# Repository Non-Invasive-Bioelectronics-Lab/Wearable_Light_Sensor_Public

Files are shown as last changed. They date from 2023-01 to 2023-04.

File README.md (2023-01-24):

# Wearable Light Sensor Public

This folder contains the version 2 development files of the wearable light monitoring device, including:

• Hardware (FR4): PCB and schematic design of the device, PCB and schematic design of the programming/debugging adaptor

• Firmware: Instructions on how to set up the environment and configure the Arduino IDE to support BL652 Bluetooth module/MCU

• Device enclosure: SolidWorks design files + .stl files for direct 3D printing

• Customised companion android app, Bluefruit LE connect (source code + .apk file)

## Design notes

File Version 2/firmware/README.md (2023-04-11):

# Arduino programming
Code to allow programming of the light monitoring device based on Laird Connectivity BL652 (Nordic semi nRF52832) bluetooth module/MCU using the Arduino IDE.
This makes use of the [Adafruit Feather nRF52 Bluefruit LE - nRF52832](https://www.adafruit.com/product/3406) product and the associated Adafruit libaries.

## Setting up enviroment
Prerequisites:
 - [Arduino IDE 1.8.15](https://www.arduino.cc/en/software) (do NOT install Windows Store version) (tested version: 1.8.15)
 - [Git](https://git-scm.com/downloads)
 - [J-Link software V6.88a and V7.20b](https://www.segger.com/downloads/jlink/#J-LinkSoftwareAndDocumentationPack) (Tested version: V6.88a)
 - [nRF Connect](https://www.nordicsemi.com/Products/Development-tools/nrf-connect-for-desktop/download) (optional)
 - [nrf command line tools](https://www.nordicsemi.com/Products/Development-tools/nRF-Command-Line-Tools/Download?lang=en#infotabs) (Tested version: 10.12.1)
 - nRF52 SDK 17.0.2 (this may not be required)
 - [Adafruit nRF52 by Adafruit Arduino Board Support Package (see below)](https://github.com/adafruit/Adafruit_nRF52_Arduino)

 To install the Adafruit nRF52 library follow the following steps:
 1. Go into Preferences
 2. Add https://adafruit.github.io/arduino-board-index/package_adafruit_index.json as an 'Additional Board Manager URL'
 3. Restart the Arduino IDE
 4. Open the Boards Manager from the Tools -> Board menu and install 'Adafruit nRF52 by Adafruit' and once it is installed, select 'Adafruit Feather nRF52832' from the Tools -> Board menu, which will update your system config to use the right compiler and settings for the nRF52.
 
 5. Delete the core folder `nrf52` installed by Board Manager in Adruino15, depending on your OS. It could be
  * macOS  : `~/Library/Arduino15/packages/adafruit/hardware`
  * Linux  : `~/.arduino15/packages/adafruit/hardware`
  * Windows: `%LOCALAPPDATA%\Arduino15\packages\adafruit\hardware`
 6. `cd <SKETCHBOOK>`, where `<SKETCHBOOK>` is your Arduino Sketch folder:
  * macOS  : `~/Documents/Arduino`
  * Linux  : `~/Arduino`
  * Windows: `~/Documents/Arduino`
 7. Create a folder named `hardware/Adafruit`, if it does not exist, and change directories to it
 8. Clone the repo from Adafruit & its submodules: 
 9. `git clone https://github.com/adafruit/Adafruit_nRF52_Arduino.git`
    
    `cd Adafruit_nRF52_Arduino`
    
    `git submodule update --init`
    
    or
    
    `git clone --recurse-submodules https://github.com/adafruit/Adafruit_nRF52_Arduino.git`

 10. Within the repo you downloaded navigate to \variants\feather_nrf52832
 11. Edit the file variant.h and comment out the line #define USE_LFXO 
 12. Change the pin definitions on line 98 - 100 to:
   ```
   #define PIN_SPI_MISO         (24)
   #define PIN_SPI_MOSI         (23)
   #define PIN_SPI_SCK          (25)
   ```
 13. Change the pin defitions on line 112 - 113 to:
   ```
   #define PIN_WIRE_SDA         (26u)
   #define PIN_WIRE_SCL         (27u)
   ```
 14. Uncomment the line #define USE_LFRC (you may need to add in '#'). This sets up the device to use the internal RC oscillator to control the BLE radio
 15. Navigate to `hardware\Adafruit\Adafruit_nRF52_Arduino` and open `programmers.txt` and change line 6 and 7 to:
 
```
nrfjprog.program.cmd=nrfjprog
nrfjprog.program.cmd.windows=nrfjprog.exe
```
 
Next step is to burn the bootloader onto the board. Plug in the board (or development board), you should be able to programme the board using either the dev kit or the dedicated J-LINK. 
Now open the Arduino IDE, go to Tools > Board > Adafruit nRF52 > Adafruit Feather nRF52832
Go to Tools > Port, and select the COM port where your debugger is connected. Note if using the dedicated J-LINK you may need to enable the COM port (J-Link Configurator, right click on device, configure, enable virtual COM port)
To flash the bootloader go to Tools > Burn Bootloader. If this fails try changing settings in Tools > Programmer and switching between J-Link for Bluefruit nRF52 and Bootloader DFU for Bluefruit nRF52
Once this has succeeded you should then be able to flash Arduino files onto the board.

To test, I recommend flashing the controller example. File > Examples > Adafruit Bluefruit nRF52 Libraries > Peripheral > controller
Hit programme. It may fail as you have to put the board in DFU mode. To do this short P0.20/SIO_20/pin 8 to ground, press and release the reset button and then remove the ground short.
Try programming again, if it fails again try switching Tools > Programmer settings as above and putting in DFU mode.

Once successfully programmed with controller example, open serial terminal and download Bluefruit Connect to your phone. Connect to Bluefruit52 > Controller > Control Pad. Press the buttons and you should see the commands appear on the serial terminal on the PC.

# Configuration 

The light monitoring device is developed based on the Adafruit Feather nRF52 Bluefruit LE [nRF52832]. Therefore, in terms of firmware and hardware configurations, it needed to be modified to meet the application requirements and allow the development of firmware based on the Adafruit nRF52 library using Arduino IDE. For example, by default, only one SPI and I2C are active on the Adafruit nRF52 library, although this project needed 2 SPI and 2 I2C according to the hardware routing.
To make the Adafruit nRF52 library ready for firmware development, follow the following steps:

First, set up the environment, then go to:

~\Documents\Arduino\hardware\adafruit\Adafruit_nRF52_Arduino\variants\feather_nrf52832
Open the variant.h with a text editor software (e.g., notepad++) and change the pin definitions on the lines below. Alternatively, you can download the pre-prepared variant.h in this folder and replace the original variant.h:

Defining pins that are different from the nrf52 feather

```
#define PIN_LED2           (11)
#define PIN_A4             (28)
#define PIN_AREF           PIN_A7
#define PIN_VBAT           PIN_A4
#define CHARG_DETECT       (18)
#define SD_DETECT          (17)
```

Adding a second SPI interface

```
#define SPI_INTERFACES_COUNT 2
#define PIN_SPI_MISO         (15)
#define PIN_SPI_MOSI         (0)
#define PIN_SPI_SCK          (13)
static const uint8_t SS    =  1 ;
static const uint8_t MOSI  = PIN_SPI_MOSI ;
static const uint8_t MISO  = PIN_SPI_MISO ;
static const uint8_t SCK   = PIN_SPI_SCK ;
#define PIN_SPI1_MISO        (23)
#define PIN_SPI1_MOSI        (24)
#define PIN_SPI1_SCK         (25)
static const uint8_t SS1   = 22 ;
static const uint8_t MOSI1 = PIN_SPI1_MOSI ;
static const uint8_t MISO1 = PIN_SPI1_MISO ;
static const uint8_t SCK1  = PIN_SPI1_SCK ;
```
Adding a second wire/I2C interface
```
#define WIRE_INTERFACES_COUNT 2
#define PIN_WIRE_SDA         (2u)
#define PIN_WIRE_SCL         (4u)
#define PIN_WIRE1_SDA        (29u)
#define PIN_WIRE1_SCL        (30u)
```
Navigate to `~\Documents\Arduino\hardware\adafruit\Adafruit_nRF52_Arduino\libraries\SPI` and open `SPI_nrf52832.cpp` with a source code editor and add the line below after `SPIClass SPI(NRF_SPIM2,  PIN_SPI_MISO,  PIN_SPI_SCK,  PIN_SPI_MOSI);` (line 227):

```
SPIClass SPI1(NRF_SPIM2,  PIN_SPI1_MISO,  PIN_SPI1_SCK,  PIN_SPI1_MOSI);
```

Navigate to `~\Documents\Arduino\hardware\adafruit\Adafruit_nRF52_Arduino\libraries\Bluefruit52Lib\src` and open `bluefruit.cpp` with a source code editor and comment line 799 (`_setConnLed(true);`) to turn off the LED during the light measurement.

In terms of hardware configuration, due to space constraints on the board, it is necessary to use a programming adaptor as the programming and UART headers are 1.27mm through hole micro terminal strips. Also, in addition to jtag pins, UART pins need to connect to the j-link for debugging/programming the Bl652 Bluetooth module/MCU.

The main firmware features are including:

•	Automatic gain control (AGC)

•	Date/time stamp

•	Real-time battery state of charge (SoC)

•	MicroSD detection

•	Precision timing

•	Command-based communication with smart devices (e.g., smartphones)

•	Auto-checking peripherals (light sensor, temp sensor, microSD card, accelerometer)

•	Saving data on a comma-separated values (CSV) file

•	Auto set date/time using a companion android app (customised Bluefruit LE Connect)

•	Built-in calibration for ADC raw values

•	Saving measurement files over BLE or USB

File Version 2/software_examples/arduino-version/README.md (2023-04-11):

# Arduino programming
Code to allow programming of the light sensor board/nRF52832 chipset using the Arduino IDE.
This makes use of the [Adafruit Feather nRF52 Bluefruit LE - nRF52832](https://www.adafruit.com/product/3406) product and the associated Adafruit libaries

## Setting up enviroment
Prerequisites:
 - Arduino IDE 1.8.13 (do NOT install Windows Store version)
 - [J-Link software V6.88](https://www.segger.com/downloads/jlink/#J-LinkSoftwareAndDocumentationPack)
 - nRF Connect
 - nRF52 SDK 17.0.2 (this may not be required)
 - [Adafruit nRF52 by Adafruit Arduino Board Support Package (see below)](https://github.com/adafruit/Adafruit_nRF52_Arduino)
 
 To install the Adafruit nRF52 library follow the following steps:
 1. Go into Preferences
 2. Add https://www.adafruit.com/package_adafruit_index.json as an 'Additional Board Manager URL'
 3. Restart the Arduino IDE
 4. Open the Boards Manager from the Tools -> Board menu and install 'Adafruit nRF52 by Adafruit'
 5. Delete the core folder `nrf52` installed by Board Manager in Adruino15, depending on your OS. It could be
  * macOS  : `~/Library/Arduino15/packages/adafruit/hardware`
  * Linux  : `~/.arduino15/packages/adafruit/hardware`
  * Windows: `%LOCALAPPDATA%\Arduino15\packages\adafruit\hardware`
 6. `cd <SKETCHBOOK>`, where `<SKETCHBOOK>` is your Arduino Sketch folder:
  * macOS  : `~/Documents/Arduino`
  * Linux  : `~/Arduino`
  * Windows: `~/Documents/Arduino`
 7. Create a folder named `hardware/Adafruit`, if it does not exist, and change directories to it
 8. Clone the repo from Adafruit & its submodules: `git clone --recurse-submodules https://github.com/adafruit/Adafruit_nRF52_Arduino.git`
 9. Within the repo you downloaded navigate to \variants\feather_nrf52832
 10. Edit the file variant.h and comment out the line #define USE_LFXO 
 11. Change the pin definitions on line 98 - 100 to:
   ```
   #define PIN_SPI_MISO         (24)
   #define PIN_SPI_MOSI         (23)
   #define PIN_SPI_SCK          (25)
   ```
 12. Change the pin defitions on line 112 - 113 to:
   ```
   #define PIN_WIRE_SDA         (26u)
   #define PIN_WIRE_SCL         (27u)
   ```
 14. Uncomment the line #define USE_LFRC (you may need to add in '#'). This sets up the device to use the internal RC oscillator to control the BLE radio
 
Next step is to burn the bootloader onto the board. Plug in the board (or development board), you should be able to programme the board using either the dev kit or the dedicated J-LINK. 
Now open the Arduino IDE, go to Tools > Board > Adafruit nRF52 > Adafruit Feather nRF52832
Go to Tools > Port, and select the COM port where your debugger is connected. Note if using the dedicated J-LINK you may need to enable the COM port (J-Link Configurator, right click on device, configure, enable virtual COM port)
To flash the bootloader go to Tools > Burn Bootloader. If this fails try changing settings in Tools > Programmer and switching between J-Link for Bluefruit nRF52 and Bootloader DFU for Bluefruit nRF52
Once this has succeeded you should then be able to flash Arduino files onto the board.

To test, I recommend flashing the controller example. File > Examples > Adafruit Bluefruit nRF52 Libraries > Peripheral > controller
Hit programme. It may fail as you have to put the board in DFU mode. To do this short P0.20/SIO_20/pin 8 to ground, press and release the reset button and then remove the ground short.
Try programming again, if it fails again try switching Tools > Programmer settings as above and putting in DFU mode.

Once successfully programmed with controller example, open serial terminal and download Bluefruit Connect to your phone. Connect to Bluefruit52 > Controller > Control Pad. Press the buttons and you should see the commands appear on the serial terminal on the PC.

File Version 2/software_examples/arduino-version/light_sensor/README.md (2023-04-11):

# light_sensor
This is the firmware based off Arduino libaries to run on the light sensor prototype (v1) board

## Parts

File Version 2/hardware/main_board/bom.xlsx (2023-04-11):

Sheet: Top Side Components
Components for Light Sensor PCB
Our order number: EEZ2177579 |  |  | PO Date: 11/12/20
Lef Ref MU201202A
Christopher Beach, christopher.beach@manchester.ac.uk, The University of Manchester
Designator | Quantity | Manufacturer 1 | Manufacturer Part Number 1 | Supplier 1 | Supplier Part Number 1 | Link 1 | Comment
Top side components
C1 | 1 | KEMET | C0603C105K3RACTU | Digi-Key | 399-7376-1-ND | https://www.digikey.co.uk/product-detail/en/kemet/C0603C105K3RACTU/399-7376-1-ND/3317410 | 0603 1 uF capacitor
C2, C8, C9 | 3 | KEMET | C0603C104K3RACTU | Digi-Key | 399-1281-1-ND | https://www.digikey.co.uk/product-detail/en/kemet/C0603C104K3RACTU/399-1281-1-ND/416057 | 0603 0.1 uF cap
C7 | 1 | AVX Corporation | TCJP105M025R0500E | Digi-Key | 478-13321-1-ND | https://www.digikey.co.uk/product-detail/en/avx-corporation/TCJP105M025R0500E/478-13321-1-ND/10062990 | 0805 1 uF tant cap
D1 | 1 | Dialight | 598-8E40-107F | Farnell | 3514756 | https://uk.farnell.com/dialight/598-8e40-107f/led-yellow-590mcd-590nm-0603/dp/3514756 | 0603 Yellow LED
J1 | 1 | JAE Electronics | DX07S016JA1R1500 | Digi-Key | 670-DX07S016JA1R1500CT-ND | https://www.digikey.co.uk/product-detail/en/jae-electronics/DX07S016JA1R1500/670-DX07S016JA1R1500CT-ND/11586676 | USB C connector
U1 | 1 | AMS | AS7341-DLGM | Digi-Key | AS7341-DLGMCT-ND | https://www.digikey.co.uk/product-detail/en/ams/AS7341-DLGM/AS7341-DLGMCT-ND/9996232 | AS7341 Light sensor
U2 | 1 | Laird Connectivity | BL652-SA-01-T/R | Digi-Key | BL652-SA-01-CT-ND | https://www.digikey.co.uk/product-detail/en/laird-connectivity-inc/BL652-SA-01-T-R/BL652-SA-01-CT-ND/6181738 | BL652 BLE Module
U3 | 1 | Analog Devices | ADXL346ACCZ-RL7 | Digi-Key | ADXL346ACCZ-RL7CT-ND | https://www.digikey.co.uk/product-detail/en/analog-devices-inc/ADXL346ACCZ-RL7/ADXL346ACCZ-RL7CT-ND/2334216 | ADXL346 Accelerometer
R1 | 1 | Panasonic Electronic Components | ERJ-3GEYJ200V | Digi-Key | P20GCT-ND | https://www.digikey.co.uk/product-detail/en/panasonic-electronic-components/ERJ-3GEYJ200V/P20GCT-ND/134656 | 0603 20 ohm resistor
R2, R3, R4 | 3 | Panasonic Electronic Components | ERJ-PA3J103V | Digi-Key | P10KBZCT-ND | https://www.digikey.co.uk/product-detail/en/panasonic-electronic-components/ERJ-PA3J103V/P10KBZCT-ND/5036237 | 0603 10k resistor
R6, R7 | 2 | Panasonic Electronic Components | ERJ-3GEYJ512V | Digi-Key | P5.1KGCT-ND | https://www.digikey.co.uk/product-detail/en/panasonic-electronic-components/ERJ-3GEYJ512V/P5-1KGCT-ND/135226 | 0603 5k1 resistor
R9 | 1 | Panasonic Electronic Components | ERJ-3GEYJ625V | Digi-Key | P6.2MGCT-ND | https://www.digikey.co.uk/product-detail/en/panasonic-electronic-components/ERJ-3GEYJ625V/P6-2MGCT-ND/282440 | 0603 6M2 resistor
R10 | 1 | Panasonic Electronic Components | ERJ-3GEYJ395V | Digi-Key | P3.9MGCT-ND | https://www.digikey.co.uk/product-detail/en/panasonic-electronic-components/ERJ-3GEYJ395V/P3-9MGCT-ND/282435 | 0603 3M9 resistor
R11 | 1 | Panasonic Electronic Components | ERJ-3GEYJ683V | Digi-Key | P68KGCT-ND | https://www.digikey.co.uk/product-detail/en/panasonic-electronic-components/ERJ-3GEYJ683V/P68KGCT-ND/134829 | 0603 68k resistor
R12 | 1 | Panasonic Electronic Components | ERJ-PA3J333V | Digi-Key | P33KBZCT-ND | https://www.digikey.co.uk/product-detail/en/panasonic-electronic-components/ERJ-PA3J333V/P33KBZCT-ND/5036309 | 0603 33k resistor
R5 | 1 | DNP
TP1, TP2, TP3, TP4, TP5, TP6 | 6 | DNP
P1, P2 | 2 | DNP |  |  |  | https://uk.farnell.com/multicomp/mc-svt1-s06-g/connector-rcpt-6pos-1row-1-27mm/dp/2852606 | 6 pin receptacle (DNP)

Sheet: Bottom Side Components
Designator | Quantity | Manufacturer 1 | Manufacturer Part Number 1 | Supplier 1 | Supplier Part Number 1 | Link 1 | Comment
Bottom side components
C3, C4, C5 | 3 | KEMET | C0603C105K3RACTU | Digi-Key | 399-7376-1-ND | https://www.digikey.co.uk/product-detail/en/kemet/C0603C105K3RACTU/399-7376-1-ND/3317410 | 0603 1 uF capacitor
C6 | 1 | KEMET | C0603C475K9PACTU | Digi-Key | 399-3482-1-ND | https://www.digikey.co.uk/product-detail/en/kemet/C0603C475K9PACTU/399-3482-1-ND/754775 | 0603 4.7 uF capacitor
U4 | 1 | Microchip Technology | MCP73812T-420I/OT | Digi-Key | MCP73812T-420I/OTCT-ND | https://www.digikey.co.uk/product-detail/en/microchip-technology/MCP73812T-420I-OT/MCP73812T-420I-OTCT-ND/1979800 | MCP73812 charge controller
U5 | 1 | Texas Instruments | TPS76318DBVT | Farnell | 3007904 | https://uk.farnell.com/texas-instruments/tps76318dbvt/v-reg-ldo-0-15a-1-8v-smd-76318/dp/3007904 | 1V8 regulator
R8 | 1 | Panasonic Electronic Components | ERJ-PB3D2002V | Digi-Key | P20429CT-ND | https://www.digikey.co.uk/product-detail/en/panasonic-electronic-components/ERJ-PB3D2002V/P20429CT-ND/6214684 | 0603 20k resistor
B1 | 1 | Multicomp | BC-2404 | Farnell | 2064669 | https://uk.farnell.com/multicomp/bc-2404/retainer-clip-24mm-smt/dp/2064669 | 2450 Cell holder
SW1 | 1 | Nidec Copal Electronics | CHS-01TB | Farnell | 2854726 | https://uk.farnell.com/nidec-copal-electronics/chs-01tb/dip-switch-1pos-spst-slide-smd/dp/2854726?ost=2854726 | Slide Switch

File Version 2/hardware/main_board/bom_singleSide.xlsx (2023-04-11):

Components for Light Sensor PCB
Our order number: EEZ2177579 |  |  | PO Date: 11/12/20
Lef Ref MU201202A
Christopher Beach, christopher.beach@manchester.ac.uk, The University of Manchester
Designator | Quantity | Manufacturer 1 | Manufacturer Part Number 1 | Supplier 1 | Supplier Part Number 1 | Link 1 | Comment
Top side components
C1 | 1 | KEMET | C0603C105K3RACTU | Digi-Key | 399-7376-1-ND | https://www.digikey.co.uk/product-detail/en/kemet/C0603C105K3RACTU/399-7376-1-ND/3317410 | 0603 1 uF capacitor
C3, C4, C5, C11 | 5 | KEMET | C0402C105K4PACTU | Onecall | 2494500 | https://onecall.farnell.com/kemet/c0402c105k4pactu/cap-1-f-16v-10-x5r-0402/dp/2494500 | 0402 1 uF capacitor
C2, C8, C9, C10, C14, C15 | 6 | TDK | CGA2B3X7R1E104K050BB | Onecall | 2210820 | https://onecall.farnell.com/tdk/cga2b3x7r1e104k050bb/cap-0-1-f-25v-10-x7r-0402/dp/2210820 | 0402 0.1 uF cap
C6, C12 | 2 | Murata | ZRB15XR61A475ME01D | Onecall | 2469394 | https://onecall.farnell.com/murata/zrb15xr61a475me01d/cap-4-7-f-10v-20-x5r-0402/dp/2469394 | 0603 4.7 uF capacitor
C7 | 1 | AVX Corporation | TCJP105M025R0500E | Digi-Key | 478-13321-1-ND | https://www.digikey.co.uk/product-detail/en/avx-corporation/TCJP105M025R0500E/478-13321-1-ND/10062990 | 0805 1 uF tant cap
C13 | 1 | Vishay | TMCP1A106KTRF | Onecall | 2491435 | https://onecall.farnell.com/vishay/tmcp1a106ktrf/cap-10-f-10v-10/dp/2491435 | 0805 10uF tant cap
D1 | 1 | Dialight | 598-8E40-107F | Farnell | 3514756 | https://uk.farnell.com/dialight/598-8e40-107f/led-yellow-590mcd-590nm-0603/dp/3514756 | 0603 Yellow LED
J1 | 1 | JAE Electronics | DX07S016JA1R1500 | Digi-Key | 670-DX07S016JA1R1500CT-ND | https://www.digikey.co.uk/product-detail/en/jae-electronics/DX07S016JA1R1500/670-DX07S016JA1R1500CT-ND/11586676 | USB C connector | Use Mouser
U1 | 1 | AMS | AS7341-DLGM | Digi-Key | AS7341-DLGMCT-ND | https://www.digikey.co.uk/product-detail/en/ams/AS7341-DLGM/AS7341-DLGMCT-ND/9996232 | AS7341 Light sensor | Use RS (18th Aug)
U2 | 1 | Laird Connectivity | BL652-SA-01-T/R | Digi-Key | BL652-SA-01-CT-ND | https://www.digikey.co.uk/product-detail/en/laird-connectivity-inc/BL652-SA-01-T-R/BL652-SA-01-CT-ND/6181738 | BL652 BLE Module | In stock
U3 | 1 | Analog Devices | ADXL362BCCZ-R2 | Digi-Key | ADXL362BCCZ-R2CT-ND | https://www.digikey.co.uk/product-detail/en/analog-devices-inc/ADXL362BCCZ-R2/ADXL362BCCZ-R2CT-ND/3828936 | ADXL346 Accelerometer
U5 | 1 | Microchip Technology | MCP73812T-420I/OT | Digi-Key | MCP73812T-420I/OTCT-ND | https://www.digikey.co.uk/product-detail/en/microchip-technology/MCP73812T-420I-OT/MCP73812T-420I-OTCT-ND/1979800 | MCP73812 charge controller | Use CPC (PO)
U4 | 1 | Texas Instruments | TPS76318DBVT | Farnell | 3007904 | https://uk.farnell.com/texas-instruments/tps76318dbvt/v-reg-ldo-0-15a-1-8v-smd-76318/dp/3007904 | 1V8 regulator
U6 | 1 | Maxim | MAX31889ALT+ | RS | 204-2520 | https://uk.rs-online.com/web/p/temperature-humidity-sensor-ics/2042520
U7 | 1 | Texas Instruments | TPS76333DBVT | Onecall | SC16625 | https://onecall.farnell.com/texas-instruments/tps76333dbvt/v-reg-ldo-0-15a-3-3v-smd-76333/dp/SC16625?ost=sc16625 | 3V3 regulator
R1 | 1 | Multicomp Pro | MCWR04X20R0FTL | Onecall | 2447134 | https://onecall.farnell.com/multicomp/mcwr04x20r0ftl/res-20r-1-0-0625w-thick-film/dp/2447134 | 0402 20 ohm resistor
R3, R4, R5 | 3 | Multicomp Pro | MCMR04X103 JTL | Onecall | 2072528 | https://onecall.farnell.com/multicomp/mcmr04x103-jtl/res-10k-5-0-0625w-0402-ceramic/dp/2072528 | 0402 10k resistor
R6, R7 | 2 | Multicomp Pro | MP000528 | Onecall | 3213460 | https://onecall.farnell.com/multicomp-pro/mp000528/res-5k1-1-0-1w-0402-thick-film/dp/3213460 | 0402 5k1 resistor
R8 | 1 | Multicomp Pro | MCWR04X2002FTL | Onecall | 2447133 | https://onecall.farnell.com/multicomp/mcwr04x2002ftl/res-20k-1-0-0625w-thick-film/dp/2447133 | 0402 20k resistor
R9 | 1 | Multicomp Pro | MCHVR02FTFY6204 | Onecall | 2825359 | https://onecall.farnell.com/multicomp/mchvr02ftfy6204/res-6m2-1-0-063w-0402-thick-film/dp/2825359 | 0402 6M2 resistor
R10 | 1 | Multicomp Pro | MCHVR02JTFY3904 | Onecall | 2825495 | https://onecall.farnell.com/multicomp/mchvr02jtfy3904/res-3m9-5-0-063w-0402-thick-film/dp/2825495 | 0402 3M9 resistor
R11 | 1 | Panasonic Electronic Components | ERJ-3GEYJ683V | Digi-Key | P68KGCT-ND | https://www.digikey.co.uk/product-detail/en/panasonic-electronic-components/ERJ-3GEYJ683V/P68KGCT-ND/134829 | 0603 68k resistor
R12 | 1 | Panasonic Electronic Components | ERJ-PA3J333V | Digi-Key | P33KBZCT-ND | https://www.digikey.co.uk/product-detail/en/panasonic-electronic-components/ERJ-PA3J333V/P33KBZCT-ND/5036309 | 0603 33k resistor
R2 | 1 | DNP
B1 | 1 | Multicomp | BC-2404 | Farnell | 2064669 | https://uk.farnell.com/multicomp/bc-2404/retainer-clip-24mm-smt/dp/2064669 | 2450 Cell holder
SW1 | 1 | Nidec Copal Electronics | CHS-01TB | Farnell | 2854726 | https://uk.farnell.com/nidec-copal-electronics/chs-01tb/dip-switch-1pos-spst-slide-smd/dp/2854726?ost=2854726 | Slide Switch
P1, P2 | 2 | DNP |  |  |  | https://uk.farnell.com/multicomp/mc-svt1-s06-g/connector-rcpt-6pos-1row-1-27mm/dp/2852606 | 6 pin receptacle (DNP)

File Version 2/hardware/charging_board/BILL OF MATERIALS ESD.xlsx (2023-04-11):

Site | Designator | Comment | Footprint | Quantity | LCSC Part No. | Man. Part no. | Link
JLCPCB | USB_FEM_1 | U262-241N-4BV64 | usbc_female | 1 | C388660 | U262-241N-4BV64 | https://jlcpcb.com/partdetail/XkbConnectivity-U262_241N4BV64/C388660
JLCPCB | USB_MALE_1 | GT-USB-8012A | PCBComponents_1 | 1 | C2982483 | GT-USB-8012A | https://jlcpcb.com/partdetail/gswitch-GT_USB8012A/C2982483
JLCPCB | D1 | SMAJ5.0A | SMA(DO-214AC) | 1 | C78401 | SMAJ5.0A/TR13 | https://jlcpcb.com/partdetail/Brightking-SMAJ5_0ATR13/C78401
JLCPCB | U1 | TPD1S414YZR | DSBGA-12 | 1 | C411873 | TPD1S414YZR | https://jlcpcb.com/partdetail/TexasInstruments-TPD1S414YZR/C411873
JLCPCB | C1 | 1 uF | "0805" | 1 | C215803 | 0805B105K500NT | https://jlcpcb.com/partdetail/216551-0805B105K500NT/C215803
JLCPCB | C2 | 2.2 uF | "0805" | 1 | C49217 | 0805F225M500NT | https://jlcpcb.com/partdetail/50225-0805F225M500NT/C49217
JLCPCB | F1 | 0466.200NRHF | FP-0466-MFG | 1 | C206985 | 0466.200NRHF | https://jlcpcb.com/partdetail/Littelfuse-0466200NRHF/C206985

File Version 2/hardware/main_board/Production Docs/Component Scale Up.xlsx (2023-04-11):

Designator | Quantity | Comment | Supplier | Part No. | 1 | 2 | 5 | 10 | 20
C1, C3, C4, C5 | 4 | 0603 1uF | Digi-Key | 399-7376-1-ND | £0.8000 | £1.6000 | £1.6440 | £5.4800 | £7.2800
C2, C8, C9, C10, C11 | 5 | 0603 0.1uF | Digi-Key | 399-1281-1-ND | £0.4000 | £0.5900 | £1.4750 | £1.6100 | £2.6300
C6 | 1 | 0603 4.7uF | Digi-Key | 399-3482-1-ND | £0.1200 | £0.2400 | £0.6000 | £0.8600 | £1.7200
C7 | 1 | 0805 1uF tant | Digi-Key | 478-13321-1-ND | £0.7800 | £1.5600 | £3.9000 | £6.1300 | £6.1300
D1 | 1 | 0603 LED | Farnell | 3514756 | £0.2784 | £0.2784 | £0.2784 | £0.5568 | £5.5680
J1 | 1 | USB C | RS | 201-7049 | £5.5700 | £5.5700 | £5.5700 | £11.1400 | £21.2400
U1 | 1 | Light Sensor | Mouser | 985-AS7341-DLGM | £6.9800 | £13.9600 | £34.9000 | £62.8000 | £125.6000
U2 | 1 | BLE Radio | Digi-Key | BL652-SA-01-CT-ND | £5.3600 | £10.7200 | £26.8000 | £53.6000 | £107.2000 | Cheap from Digikey, stock expected 26th May
U3 | 1 | Accelerometer | Digi-Key | ADXL346ACCZ-RL7CT-ND | £4.6500 | £9.3000 | £23.2500 | £41.7600 | £83.5200
U4 | 1 | Charge Controller | Mouser | 579-MCP73812T-420IOT | £0.4350 | £0.8700 | £2.1750 | £4.3500 | £8.7000
U5 | 1 | 1V8 regulator | Digi-Key | 296-2700-1-ND | £0.7100 | £1.4200 | £3.5500 | £6.3400 | £12.6800
U6 | 1 | Temperature sensor | Digi-Key | 175-MAX31889ALT+-ND | £2.4900 | £4.9800 | £12.4500 | £22.3400 | £44.6800
U7 | 1 | Flash Memory | Digi-Key | 1265-1280-1-ND | £1.0700 | £2.1400 | £5.3500 | £9.7600 | £19.5200
R1 | 1 | 0603 20R | Digi-Key | P20GCT-ND | £0.0700 | £0.1400 | £0.2400 | £0.2400 | £0.4800
R2, R3, R4 | 3 | 0603 10k | Digi-Key | P10KGCT-ND | £0.2100 | £0.4200 | £0.9750 | £1.9500 | £2.4800
R6, R7 | 2 | 0603 5k1 | Digi-Key | P5.1KGCT-ND | £0.2800 | £0.2900 | £0.2900 | £0.5800 | £1.1600
R8 | 1 | 0603 20k | Digi-Key | P20KGCT-ND | £0.0700 | £0.1400 | £0.2600 | £0.2600 | £0.5200
R9 | 1 | 0603 6M2 | Digi-Key | P6.2MGCT-ND | £0.0700 | £0.1400 | £0.1700 | £0.1700 | £0.3400
R10 | 1 | 0603 3M9 | Digi-Key | P3.9MGCT-ND | £0.0700 | £0.1400 | £0.2400 | £0.2400 | £0.4800
R11 | 1 | 0603 68k | Digi-Key | P68KGCT-ND | £0.0700 | £0.1400 | £0.2400 | £0.2400 | £0.4800
R12 | 1 | 0603 33k | Digi-Key | P33KGCT-ND | £0.0700 | £0.1400 | £0.2400 | £0.2400 | £0.4800
SW1 | 1 | Slide Switch | Digi-Key | 563-1004-1-ND | £0.6500 | £1.3000 | £3.2500 | £6.2400 | £12.4800
B1 | 1 | Battery Holder | Farnell | 2064669 | £0.6480 | £1.2960 | £3.2400 | £6.4800 | £12.9600
P1, P2 | 2 | Programming Header | Farnell | 2852606 | £2.0520 | £2.0520 | £2.0520 | £4.1040 | £8.2080
NO REF | 1 | LiIon Coin Cell | Farnell | 2009025 | £3.1200 | £6.2400 | £15.6000 | £28.6800 | £57.3600
Total cost |  |  |  |  | £37.0234 | £65.6664 | £148.7394 | £276.1508 | £543.8960
Price per Unit |  |  |  |  | £37.0234 | £32.8332 | £29.7479 | £27.6151 | £27.1948

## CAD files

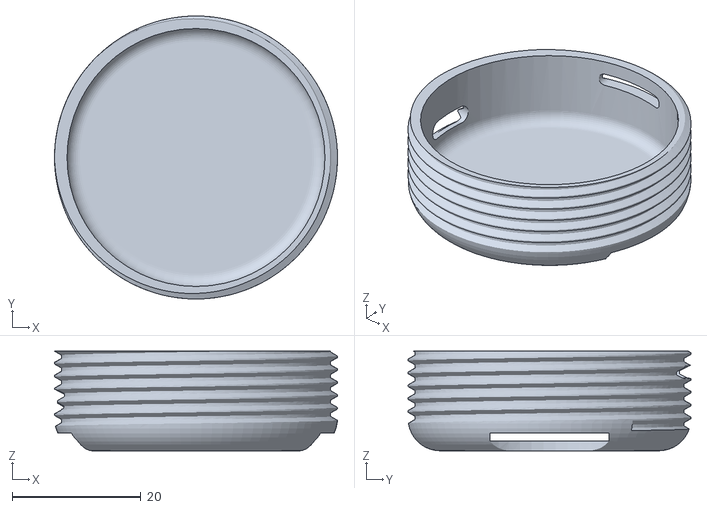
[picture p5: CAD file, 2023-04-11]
Version 2/case/1-20-F.STL
44.0 x 44.0 x 15.5

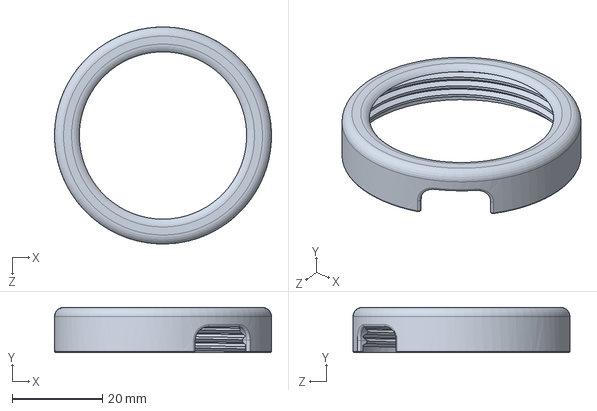
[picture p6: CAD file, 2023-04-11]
Version 2/case/SolidWork files/3 - 27-06-2022_low profile.SLDPRT
48.0 x 10.0 x 48.0 mm

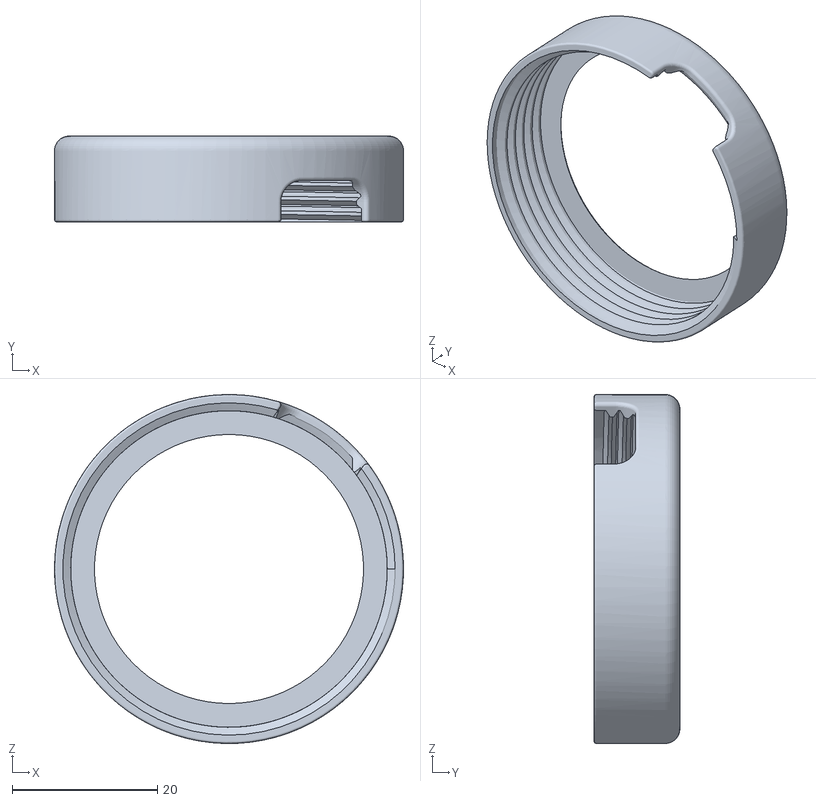
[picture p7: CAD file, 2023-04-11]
Version 2/case/3.STL
48.0 x 11.8 x 48.0

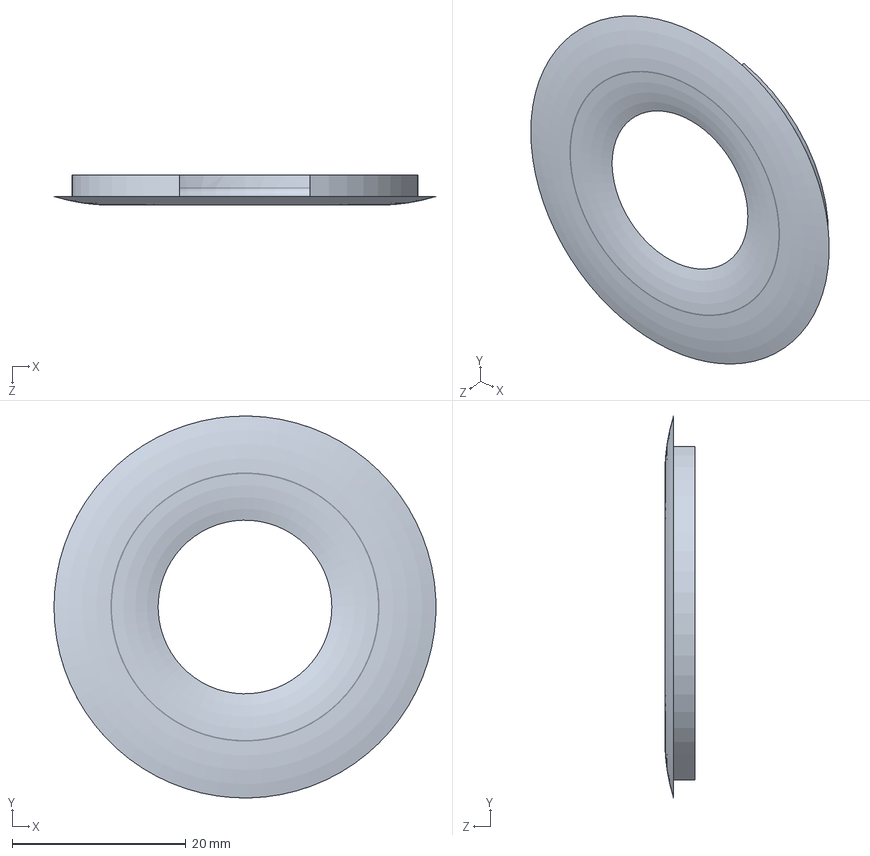
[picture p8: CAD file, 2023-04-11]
Version 2/case/SolidWork files/2 - 11-05-2022.SLDPRT
44.0 x 44.0 x 3.50 mm

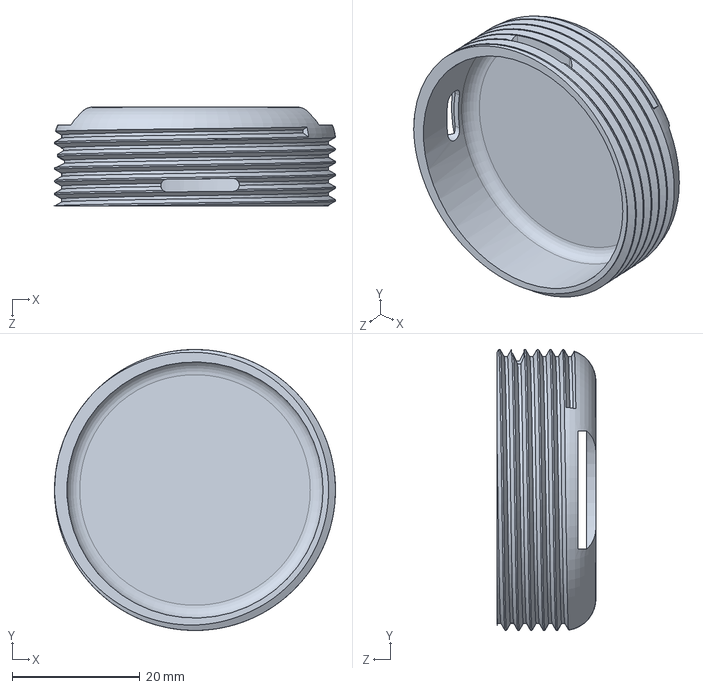
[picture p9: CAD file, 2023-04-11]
Version 2/case/SolidWork files/1 - 11-05-2022.SLDPRT
44.0 x 44.0 x 15.5 mm

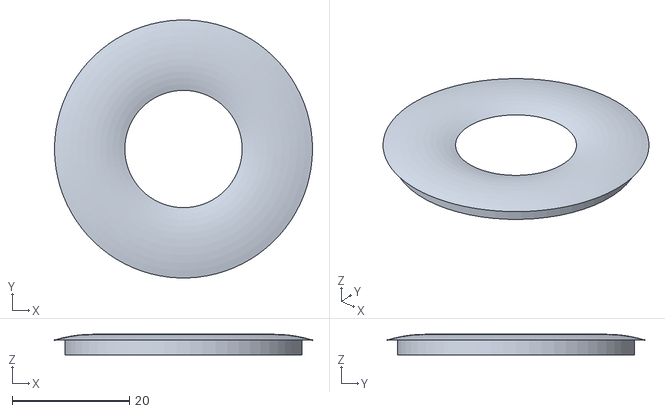
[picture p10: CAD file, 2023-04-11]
Version 2/case/2.STL
44.0 x 44.0 x 3.50

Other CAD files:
Version 2/case/1-3-F.STL
Version 2/case/SolidWork files/3 - 11-05-2022.SLDPRT
Version 2/case/1-8-F.STL
Version 2/case/3 - low profile.STL
Version 2/case/1-2-F.STL
Version 2/case/1-6-F.STL
Version 2/case/1-18-F.STL
Version 2/case/1-4-F.STL
Version 2/case/1-13-F.STL
Version 2/case/1-16-F.STL
Version 2/case/1-15-F.STL
Version 2/case/1-12-F.STL
Version 2/case/1-1-F.STL
Version 2/case/1-10-F.STL
Version 2/case/1-11-F.STL
Version 2/case/1-14-F.STL
Version 2/case/1-17-F.STL
Version 2/case/1-19-F.STL
Version 2/case/1-5-F.STL
Version 2/case/1-7-F.STL
Version 2/case/1-9-F.STL
Version 2/case/2 - updated (with cut off) 11-05-2022.STL
Version 2/case/3 - updated - 11-05-2022.STL
Version 2/case/SolidWork files/2 - 11-05-2022.STL
Version 2/case/SolidWork files/3 - 11-05-2022.STL
Version 2/case/SolidWork files/3 - 27-06-2022_low profile.STL

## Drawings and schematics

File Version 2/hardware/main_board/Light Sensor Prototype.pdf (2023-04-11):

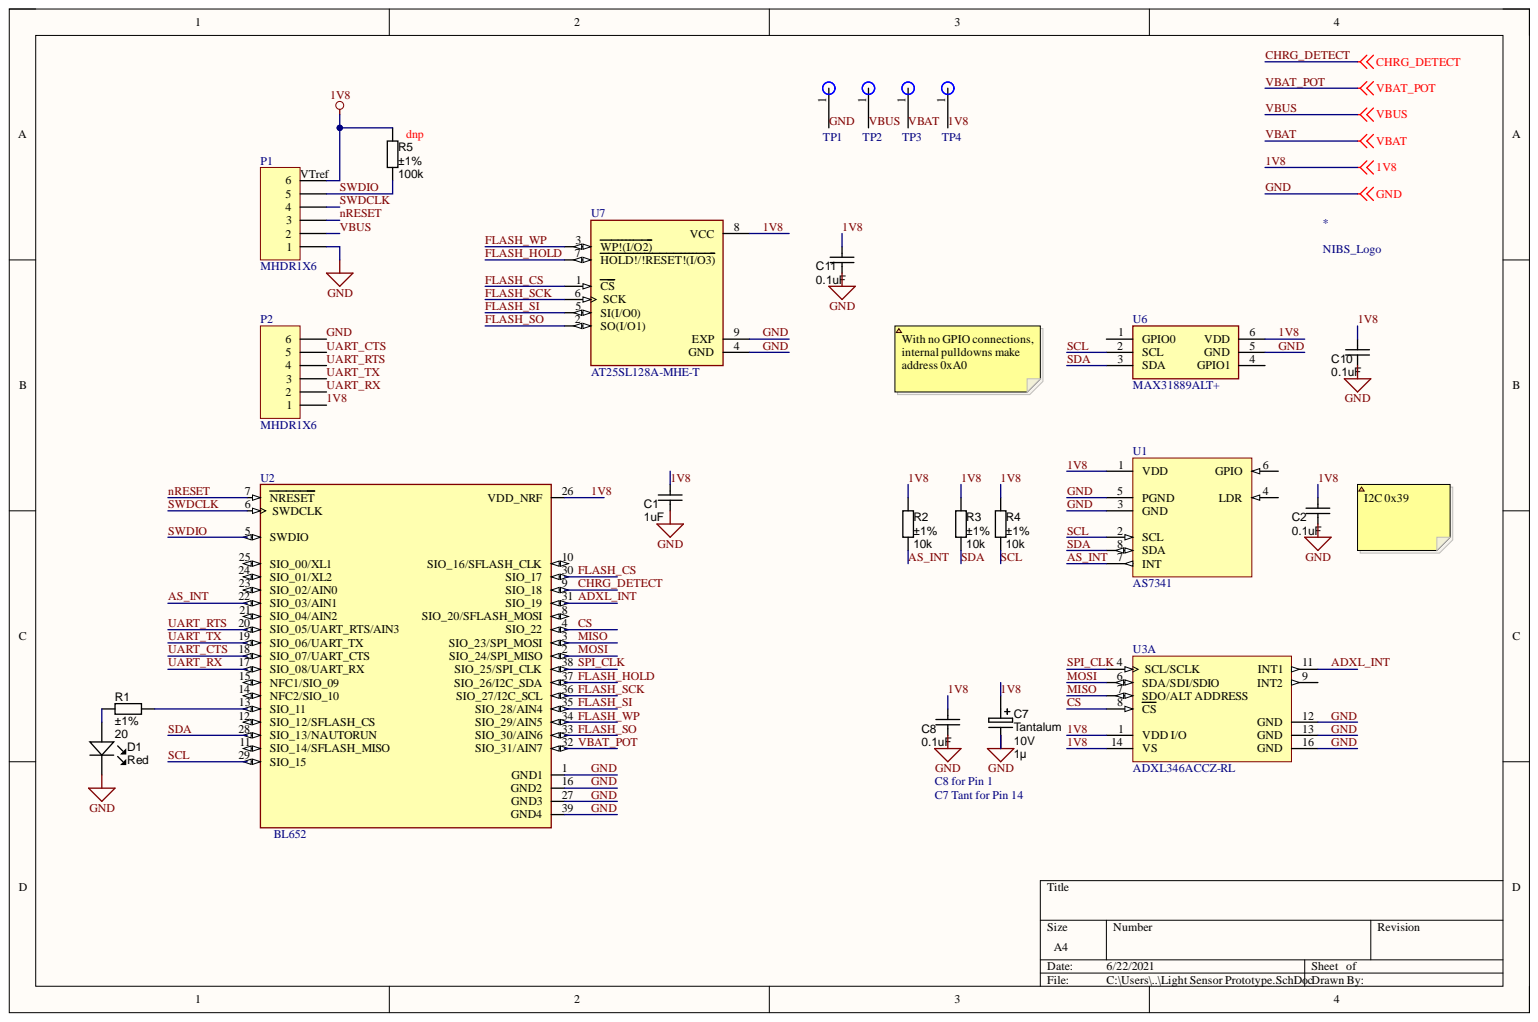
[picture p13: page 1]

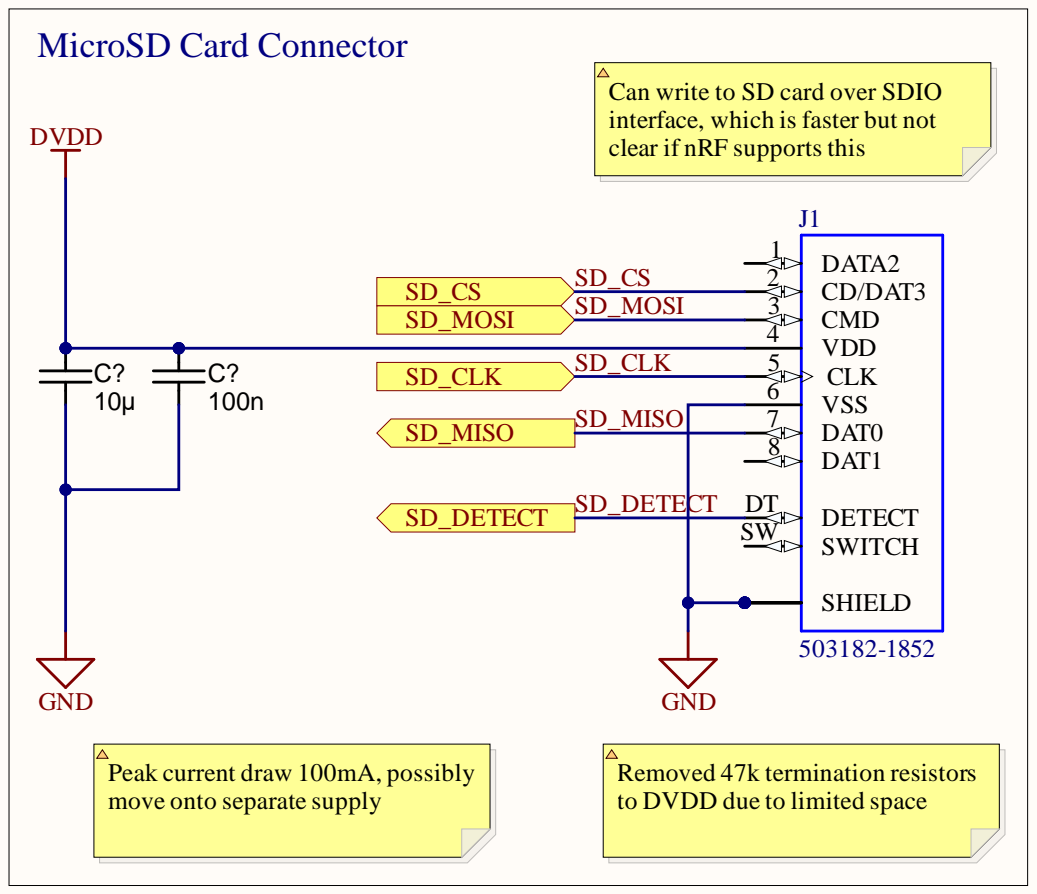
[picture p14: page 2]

Can write to SD card over SDIO
interface, which is faster but not
clear if nRF supports this

Peak current draw 100mA, possibly
move onto separate supply

Removed 47k termination resistors
to DVDD due to limited space

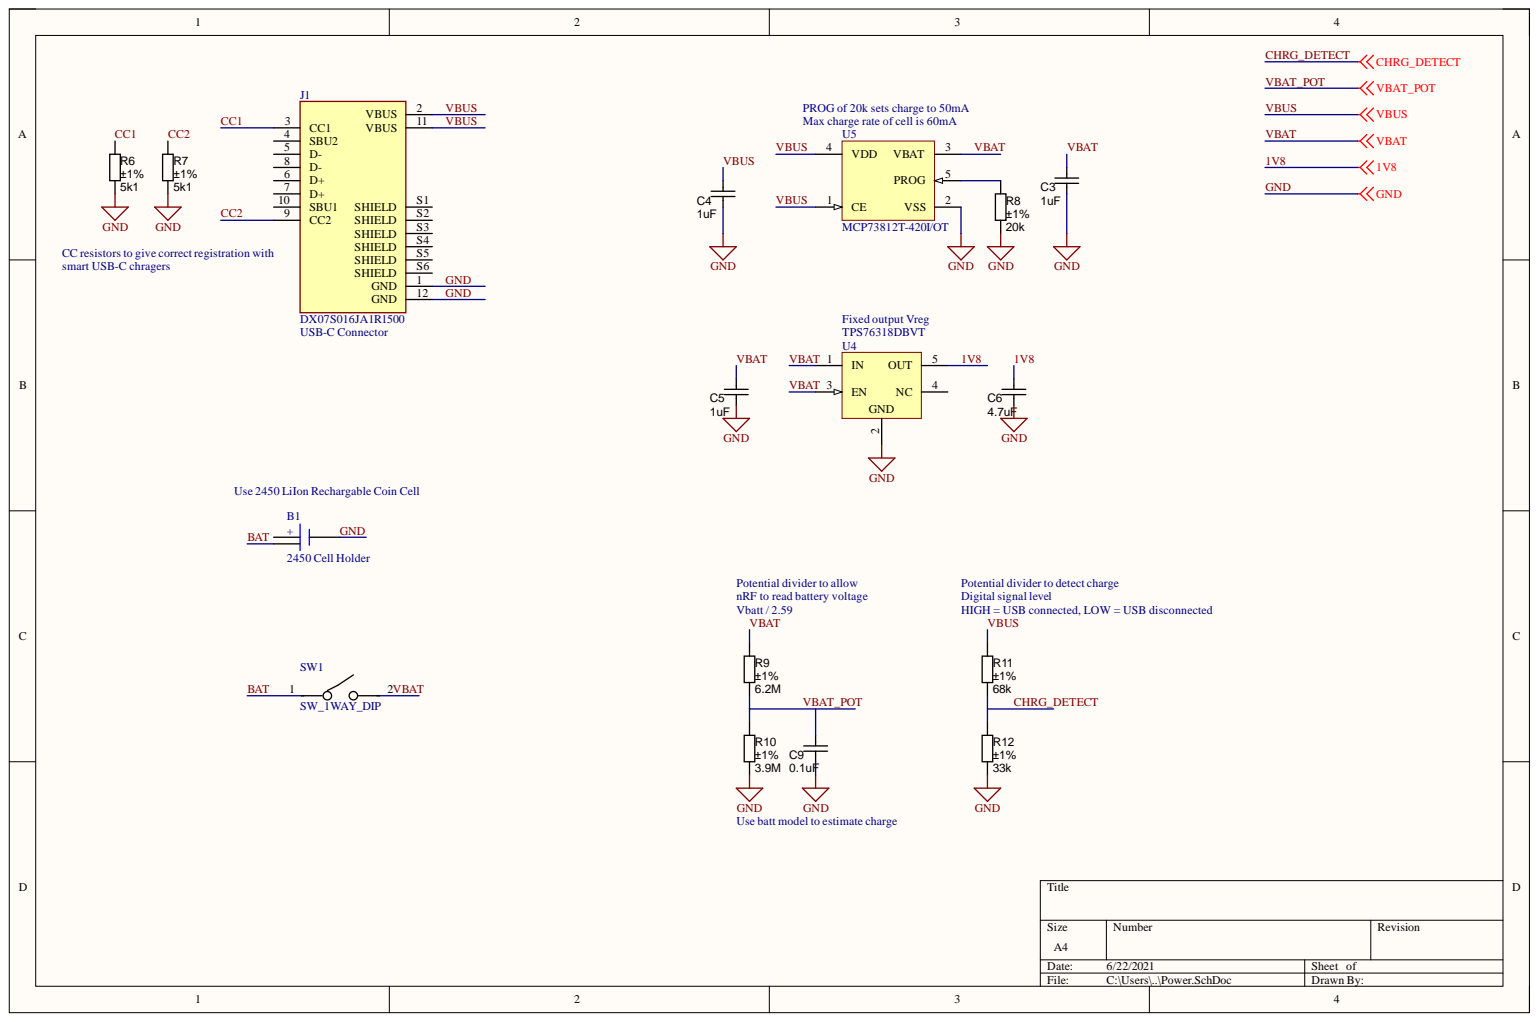
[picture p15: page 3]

PROG of 20k sets charge to 50mA
Max charge rate of cell is 60mA

CC resistors to give correct registration with
smart USB-C chragers

Use 2450 LiIon Rechargable Coin Cell

Potential divider to allow
nRF to read battery voltage
Vbatt / 2.59
VBAT

Potential divider to detect charge
Digital signal level
HIGH = USB connected, LOW = USB disconnected
VBUS

GND
Use batt model to estimate charge

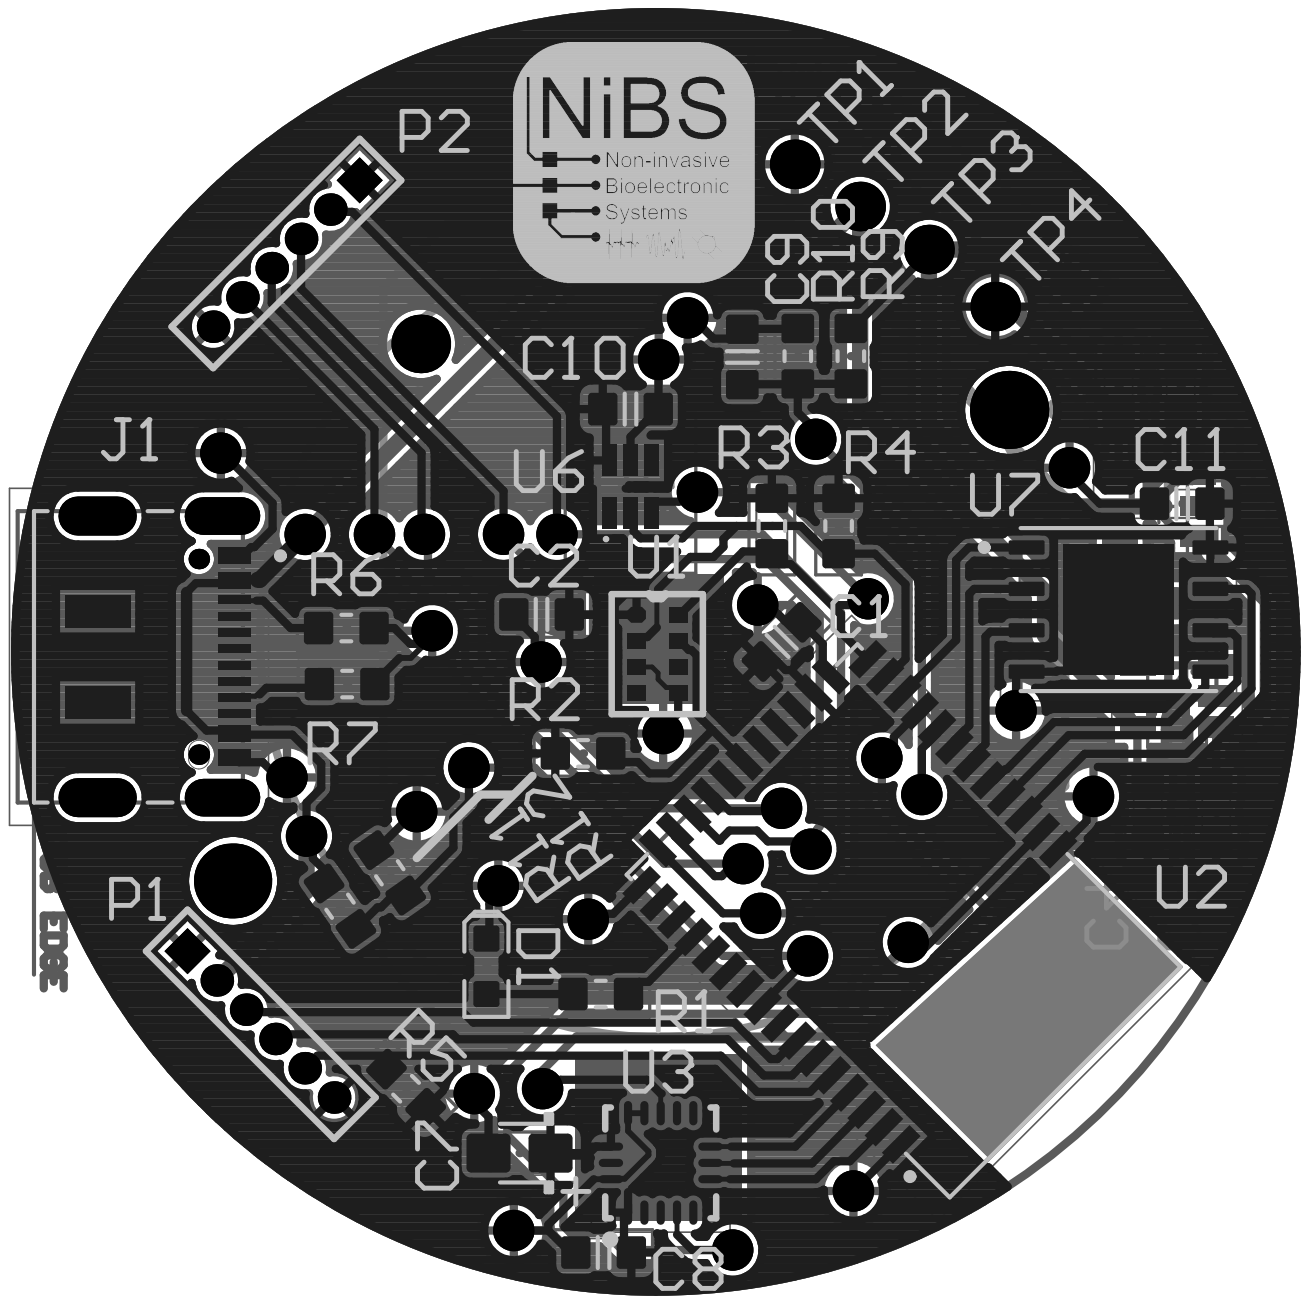
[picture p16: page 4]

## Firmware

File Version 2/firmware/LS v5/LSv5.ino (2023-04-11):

#include <bluefruit.h>
#include <Adafruit_AS7341.h>
#include <LibPrintf.h>
#include <SPI.h>
#include <SD.h>
#include "Time.h"
#include "TimeLib.h"
#include <Wire.h>
#include <ADXL362.h>


// BLE Service
//BLEDfu  bledfu;  // OTA DFU service
BLEDis  bledis;  // device information
BLEUart bleuart; // uart over ble

TwoWire *wi = &Wire1;
ADXL362 ACC; 
Adafruit_AS7341 as7341;
uint8_t light_status;
uint8_t temp_status;
bool Connected = false;
bool sendData = false;
bool state = false;
bool ACC_failed = false;
float correctionGain [12] = {1.06, 1.05, 1.05, 1.05, 1.02, 1.02, 1.01, 1.00, 1.00, 0.99, 0.96};
float correctionFactor [12] = {1,1,1,1,1,1,1,1,1,1,1};
float offsetValues [12] = {0,0,0,0,0,0,0,0,0,0,0};
uint16_t readings[12];
bool timer_start = false;
uint8_t sd_first;
unsigned int A_gain;
uint8_t currentGain = 5;
uint8_t maxGain = 10;
bool RawValueSaturated = false;
bool RawValueNoise = false;
bool iPhone_device = false;
uint8_t newGain = 0;
char central_name[32] = { 0 };
unsigned int A_int;
uint16_t ch[12];
const int chipSelect = 1;
char dataStr[220];
char dataStr1[170];
char num_sam[11];
char filename[13] = "LS14_1.csv";
char num[5];
char timeStr[19] = "";
int acc_status = 0;
char SoC_buf[25];
char time_cent[22];
char setting[35];
volatile bool event = false; 
bool st_check = false;
bool dis_check = true;
bool TS_Failed = false;
char *col_names[] = {"Date", "Time","SoC","Temp", "Gain", "F1", "F2", "F3",
                         "F4", "F5", "F6", "F7" , "F8" , "Clear", "NIR", "accX" , "accY", "accZ",
                        };
char *channel_names[13] = {"F1", "F2", "F3",
                         "F4"," "," ", "F5", "F6", "F7" , "F8" , "Clr", "NIR"
                        };
float corr_counts[12];
char data_buf[25];
int j = 1;
uint8_t vbat_per;
String yearr;
int finder;
String date_parse;
char * str;
char * str_cent;
bool s_time;
uint32_t vbat_pin = A4;
time_t timeNow;
uint8_t presecond;         
#define VBAT_MV_PER_LSB   (0.73242188F)   // 3.0V ADC range and 12-bit ADC resolution = 3000mV/4096
#define VBAT_DIVIDER      (0.71387696F)   // 2M(499) + 0.806M (200k) voltage divider on VBAT = (2M / (0.806M + 2M))
#define VBAT_DIVIDER_COMP (1.400F)        // Compensation factor for the VBAT divider
#define WAKE_HIGH_PIN CHARG_DETECT
#define REAL_VBAT_MV_PER_LSB (VBAT_DIVIDER_COMP * VBAT_MV_PER_LSB)

void configBLE()
{
  // Setup the BLE LED to be enabled on CONNECT
  // Note: This is actually the default behavior, but provided

  
  // here in case you want to control this LED manually via PIN 11
  
  Bluefruit.autoConnLed(true);
  
  // Config the peripheral connection with maximum bandwidth
  // more SRAM required by SoftDevice
  // Note: All config***() function must be called before begin() 
  Bluefruit.configPrphBandwidth(BANDWIDTH_MAX);

  Bluefruit.begin();
  // TX power -40, -20, -16, -12, -8, -4, 0, 3, 4
  Bluefruit.setTxPower(4);    // Check bluefruit.h for supported values
  Bluefruit.setName("NIBS LS14");
  //Bluefruit.setName(getMcuUniqueID()); // useful testing with multiple central connections
  Bluefruit.Periph.setConnectCallback(connect_callback);
  Bluefruit.Periph.setDisconnectCallback(disconnect_callback);

  // To be consistent OTA DFU should be added first if it exists
  //bledfu.begin();

  // Configure and Start Device Information Service
  bledis.setManufacturer("NIBS");
  bledis.setModel("LS v3.0");
  bledis.begin();
}
void configBLEUart() {
  // Configure and Start BLE Uart Service
  bleuart.begin();
}
void configAdv() {
  // Set up and start advertising
  startAdv();
}

void set_gain(uint8_t gain) {
  switch (gain) {
  case 0:
  as7341.setGain(AS7341_GAIN_0_5X);
    break;
  case 1:
  as7341.setGain(AS7341_GAIN_1X);
    break;
  case 2:
  as7341.setGain(AS7341_GAIN_2X);
    break;
  case 3:
  as7341.setGain(AS7341_GAIN_4X);
    break;
  case 4:
  as7341.setGain(AS7341_GAIN_8X);
    break;
  case 5:
  as7341.setGain(AS7341_GAIN_16X);
    break;
  case 6:
  as7341.setGain(AS7341_GAIN_32X);
    break;
  case 7:
  as7341.setGain(AS7341_GAIN_64X);
    break;
  case 8:
  as7341.setGain(AS7341_GAIN_128X);
    break;
  case 9:
  as7341.setGain(AS7341_GAIN_256X);
    break;
  case 10:
  as7341.setGain(AS7341_GAIN_512X);
    break;
  }
}
void default_set() {
  as7341.setATIME(0);
  as7341.setASTEP(65466);
  set_gain(currentGain);
}
void find_gain() {
  as7341_gain_t gain = as7341.getGain();
  switch (gain) {
  case AS7341_GAIN_0_5X:
  A_gain = 0;
    break;
  case AS7341_GAIN_1X:
    A_gain = 1;
    break;
  case AS7341_GAIN_2X:
    A_gain = 2;
    break;
  case AS7341_GAIN_4X:
    A_gain = 4;
    break;
  case AS7341_GAIN_8X:
    A_gain = 8;
    break;
  case AS7341_GAIN_16X:
    A_gain = 16;
    break;
  case AS7341_GAIN_32X:
    A_gain = 32;
    break;
  case AS7341_GAIN_64X:
    A_gain = 64;
    break;
  case AS7341_GAIN_128X:
    A_gain = 128;
    break;
  case AS7341_GAIN_256X:
    A_gain = 256;
    break;
  case AS7341_GAIN_512X:
    A_gain = 512;
    break;
  }
}

void AGC(){
uint8_t saturationGain = 11;
if (currentGain > maxGain){
currentGain = maxGain;
}

while (true){
  uint16_t AGC_readings[12];
  if (!as7341.readAllChannels(AGC_readings)){
    //Serial.println("Error reading all channels!");
    return;
  } 
     for(uint8_t i = 0; i < 12; i++) {
    if(i == 4 || i == 5) continue;
    if (AGC_readings[i] >= 65467) {
      RawValueSaturated = true;
    } 
    if (AGC_readings[i] <= 10000) {
      RawValueNoise = true;  
    } 
}
  if(RawValueSaturated){
    if (currentGain == 0){
      RawValueSaturated = false;
    break;
    }
   
    if (currentGain < saturationGain){
    saturationGain = currentGain;
    }
    currentGain--;
    set_gain(currentGain);
    RawValueSaturated = false;
  }
else if (RawValueNoise){
  if (currentGain == maxGain){
    RawValueNoise = false;
    break;
    }
      newGain = ((maxGain + currentGain) / 2.0 + 0.5);
      if (newGain == currentGain)
      {
      newGain++;
      }

      if (newGain >= saturationGain){
        RawValueNoise = false;
      break;
      }
    currentGain = newGain;
    set_gain(currentGain);
    RawValueNoise = false;
} 
}
}


void configAS7431() {
  if (!as7341.begin()) {
    //Serial.println("Could not find AS7341");
    while (1) {
      delay(10);
    }
  }
  default_set();
}

void configTimer() {
  // Configure TIMER2 which controls light sensor sampling (TIMER0 is used by softdevice)
  NRF_TIMER2->TASKS_STOP = 1;                         // Stop timer
  NRF_TIMER2->MODE = TIMER_MODE_MODE_Timer;           // Set timer to timer mode
  NRF_TIMER2->TASKS_CLEAR = 1;                        // Clear the task first so it's usable later
  NRF_TIMER2->PRESCALER = 9;                          // Prescaler value maximum is 9, f_tick = 16MHz / 2 ^ n
  NRF_TIMER2->BITMODE = TIMER_BITMODE_BITMODE_24Bit;  // Set 16 bit timer resolution
  NRF_TIMER2->CC[0] = 31250 * 30;                      // Set value for compare first compare register (f_ticks * CC)
  // NRF_TIMER2->CC[1] = 65535;                       // Can set up to 6 compare registers
  NRF_TIMER2->INTENSET = TIMER_INTENSET_COMPARE0_Enabled << TIMER_INTENSET_COMPARE0_Pos;          // Enable COMAPRE0 Interrupt
  NRF_TIMER2->SHORTS = (TIMER_SHORTS_COMPARE0_CLEAR_Enabled << TIMER_SHORTS_COMPARE0_CLEAR_Pos);  // Count then Complete mode enabled
  NVIC_EnableIRQ(TIMER2_IRQn);                        // Enable interrupts
  //NRF_TIMER2->TASKS_START = 1;                        // Start timer
}



void setup(){ 
  nrf_gpio_cfg(30, NRF_GPIO_PIN_DIR_INPUT, NRF_GPIO_PIN_INPUT_CONNECT, NRF_GPIO_PIN_PULLUP, NRF_GPIO_PIN_S0D1, NRF_GPIO_PIN_NOSENSE);
  nrf_gpio_cfg(29, NRF_GPIO_PIN_DIR_INPUT, NRF_GPIO_PIN_INPUT_CONNECT, NRF_GPIO_PIN_PULLUP, NRF_GPIO_PIN_S0D1, NRF_GPIO_PIN_NOSENSE);
  nrf_gpio_cfg_input(18,NRF_GPIO_PIN_NOPULL);
  Serial.begin(115200);
  pinMode(SD_DETECT, INPUT);
  Wire1.begin();
  configBLE();
  configBLEUart();
  configAdv();
  configAS7431();
  configTimer();
  pinMode(4, OUTPUT);
  for (int i = 0; i < 18; i++) {
  strcat(dataStr1, col_names[i]);
  strcat( dataStr1, ", ");
  s_time = false;
  }
}

void startAdv(void)
{
  // Advertising packet
  Bluefruit.Advertising.addFlags(BLE_GAP_ADV_FLAGS_LE_ONLY_GENERAL_DISC_MODE);
  Bluefruit.Advertising.addTxPower();

  // Include bleuart 128-bit uuid
  Bluefruit.Advertising.addService(bleuart);

  // Secondary Scan Response packet (optional)
  // Since there is no room for 'Name' in Advertising packet
  Bluefruit.ScanResponse.addName();

  /* Start Advertising
     - Enable auto advertising if disconnected
     - Interval:  fast mode = 20 ms, slow mode = 152.5 ms
     - Timeout for fast mode is 30 seconds
     - Start(timeout) with timeout = 0 will advertise forever (until connected)

     For recommended advertising interval
     https://developer.apple.com/library/content/qa/qa1931/_index.html
  */
  Bluefruit.Advertising.restartOnDisconnect(true);
  Bluefruit.Advertising.setInterval(32, 244);    // in unit of 0.625 ms
  Bluefruit.Advertising.setFastTimeout(2);      // number of seconds in fast mode
  Bluefruit.Advertising.start(0);                // 0 = Don't stop advertising after n seconds
}

void loop()
{
   
   if(Connected && s_time == false){
   init_set_time();
   }
   
  

    
   
  if(state){
    Bluefruit.Advertising.start(2);
  }


  
  unsigned long startloop = millis();
  if(state == false && Connected){
  
  bleuart.write("Send ""s/"" to start the measurement\n", 36);
  delay(4000);
  }
  if(Connected){
  read_cent();
  }
  if (sendData && state) {
  sendData = false;
  enable_per();
  send_data();
  //Serial.println("after send_data");
  }
  check_batt();
if(state){
  
  unsigned long datasend = millis();
  unsigned long Millis = datasend - startloop;
  if(Millis <= 2000){
  uint32_t delaytime = 2000 - (int)Millis;
  delay(delaytime);
  
  
  
  }
  else{
    
  }
  unsigned long endloop = millis();
  unsigned long Millisend = endloop - startloop;
  if(Millisend == 1999){
    delay(1);
  }
    else{
    
  }
 
  unsigned long endlooop = millis();
  unsigned long Millisendd = endlooop - startloop;
  //printf(" end loop time: %d\n",Millisendd);

    if(Millisendd < 30000){
  uint32_t sleeptime = 30000 - (int)Millisendd;
  //Serial.print("sleeptime: ");
  //Serial.println(sleeptime);
  disable_per(); 
  delay(sleeptime);
  
    }
    else{
      
      }
}
/*LED turns ON when connected to a charger
  if(nrf_gpio_pin_read(18) == HIGH){
  Bluefruit.autoConnLed(false);
  digitalWrite(11, HIGH);
  delay(500);
  digitalWrite(11, LOW);
  delay(500);
  }
  */

}

void send_data(void)
{

  //vbatt_per();
  uint16_t data;
  String str_data;
  char buf[12];
  //check_SD();

  memset(dataStr, 0, 210);
  timeNow = now();
  //showTime(timeNow);
  //--------date
  //Serial.println(second());
  if(presecond == second()){
    //Serial.println("presecond");
    delay(60);
    timeNow = now();
    //showTime(timeNow);
    //Serial.println("I'm in the second if");
  }
  
  sprintf(timeStr,"%d/%d/%d, %d:%d:%d",day(),month(),year(),hour(),minute(),second());
  if(Connected){ 
  bleuart.write(timeStr, 20);
  bleuart.write("\n", 1);
  }
  presecond = second();
  strcat(dataStr, timeStr);
  strcat( dataStr, ", ");
  memset(timeStr, 0, 20);
  
  
//----------bat level
  vbatt_per();
  strcat( dataStr,SoC_buf);
  strcat( dataStr, ", ");
        
  memset(SoC_buf, 0, 25);
  if(vbat_per < 20){
    sprintf(SoC_buf, "SoC = Low(%d%%)", vbat_per);
  }
  else{
    sprintf(SoC_buf, "SoC = %d%%", vbat_per);
  }
  if(Connected){ 
  bleuart.write(SoC_buf, 25);
  bleuart.write("\n", 1);
  }
             
  //Serial.println(SoC_buf);
//----------------------------------batt end
//------------------ temp
float temp;
if(TS_Failed == true){
  temp = Read_ACCTemp();
}
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

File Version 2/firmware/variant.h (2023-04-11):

 /*
  Copyright (c) 2014-2015 Arduino LLC.  All right reserved.
  Copyright (c) 2016 Sandeep Mistry All right reserved.
  Copyright (c) 2018, Adafruit Industries (adafruit.com)

  This library is free software; you can redistribute it and/or
  modify it under the terms of the GNU Lesser General Public
  License as published by the Free Software Foundation; either
  version 2.1 of the License, or (at your option) any later version.
  This library is distributed in the hope that it will be useful,
  but WITHOUT ANY WARRANTY; without even the implied warranty of
  MERCHANTABILITY or FITNESS FOR A PARTICULAR PURPOSE.
  See the GNU Lesser General Public License for more details.
  You should have received a copy of the GNU Lesser General Public
  License along with this library; if not, write to the Free Software
  Foundation, Inc., 51 Franklin St, Fifth Floor, Boston, MA  02110-1301  USA
*/

#ifndef _VARIANT_FEATHER52832_
#define _VARIANT_FEATHER52832_

/** Master clock frequency */
#define VARIANT_MCK       (64000000ul)

//#define USE_LFXO      // Board uses 32khz crystal for LF
#define USE_LFRC    // Board uses RC for LF

/*----------------------------------------------------------------------------
 *        Headers
 *----------------------------------------------------------------------------*/

#include "WVariant.h"

#ifdef __cplusplus
extern "C"
{
#endif // __cplusplus

// Number of pins defined in PinDescription array
#define PINS_COUNT           (32u)
#define NUM_DIGITAL_PINS     (32u)
#define NUM_ANALOG_INPUTS    (8u)
#define NUM_ANALOG_OUTPUTS   (0u)

// LEDs
#define PIN_LED1             (27)
#define PIN_LED2             (11)

#define LED_BUILTIN          PIN_LED1
#define LED_CONN             PIN_LED2

#define LED_RED              PIN_LED1
#define LED_BLUE             PIN_LED2

#define LED_STATE_ON         1         // State when LED is litted

/*
 * Analog pins
 */
#define PIN_A0               (2)
#define PIN_A1               (3)
#define PIN_A2               (4)
#define PIN_A3               (5)
#define PIN_A4               (28)
#define PIN_A5               (29)
#define PIN_A6               (30)
#define PIN_A7               (31)

static const uint8_t A0  = PIN_A0 ;
static const uint8_t A1  = PIN_A1 ;
static const uint8_t A2  = PIN_A2 ;
static const uint8_t A3  = PIN_A3 ;
static const uint8_t A4  = PIN_A4 ;
static const uint8_t A5  = PIN_A5 ;
static const uint8_t A6  = PIN_A6 ;
static const uint8_t A7  = PIN_A7 ;
#define ADC_RESOLUTION    14

// Other pins
#define PIN_AREF           PIN_A7
#define PIN_VBAT           PIN_A4
#define PIN_NFC1           (9)
#define PIN_NFC2           (10)
#define CHARG_DETECT       (18)
#define SD_DETECT          (17)

static const uint8_t AREF = PIN_AREF;

/*
 * Serial interfaces
 */
#define PIN_SERIAL_RX       (8)
#define PIN_SERIAL_TX       (6)

/*
 * SPI Interfaces
 */
#define SPI_INTERFACES_COUNT 2
/*
#define PIN_SPI_MISO         (23)
#define PIN_SPI_MOSI         (24)
#define PIN_SPI_SCK          (25)

static const uint8_t SS   = 22 ;
*/


#define PIN_SPI_MISO         (15)
#define PIN_SPI_MOSI         (0)
#define PIN_SPI_SCK          (13)

static const uint8_t SS   = 1 ;
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

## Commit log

2023-04-11 Bulk copy of files from private repo
    [1 - 11-05-2022.SLDPRT, 1-1-F.STL, 1-10-F.STL, 1-11-F.STL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]
2023-09-25 Add files via upload
    Added charger case
